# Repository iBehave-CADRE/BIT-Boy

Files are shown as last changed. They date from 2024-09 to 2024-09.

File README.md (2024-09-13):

# BITboy

A handheld oscilloscope and behavioral setup debugger for neuroscientists. Your every-day companion for trouble shooting and setting up experimental instruments.

Read and write both analog and digital signals with ease. Check continuity in electronic circuits with the continuity checker. It can be used as a handheld oscilloscope or connected to your pc on a desk for higher resolution.

General disclaimer: Our BITboy is designed to work in a range of 0-5V and will take damage if connected to higher loads. Therefore, please be careful. We are planning a future version with overvoltage protection.

<p align="center">
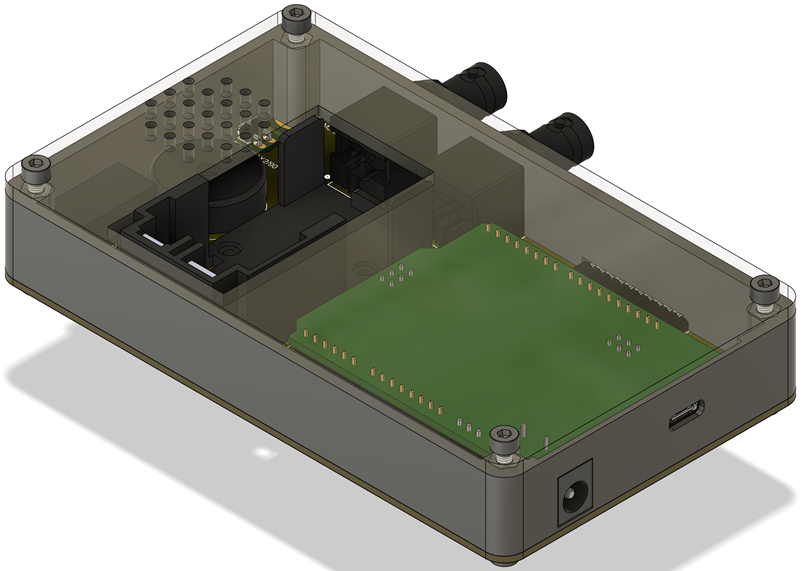
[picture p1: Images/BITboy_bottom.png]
  
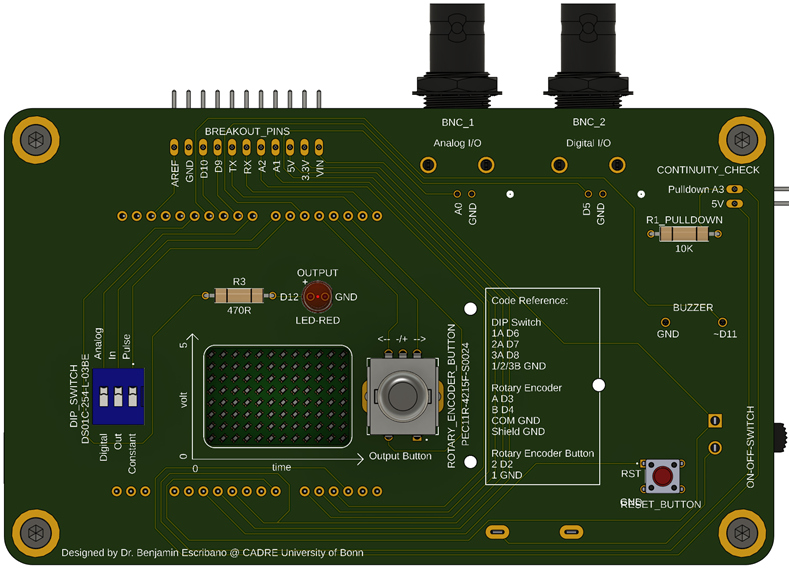
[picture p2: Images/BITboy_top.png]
  
</p>

All provided files are in metric units (mm). The case can be 3D printed, while the cover can be lasercut or printed. The design aims at maximum reproduxibility with low total cost.

### Commercial Parts List

| Item | Quantity | Notes | Product Example Link |
| :---: | :---: | :---: | :---: |
| PCB | 1 piece | [custom design](PCB) | [eurocircuits.com](https://www.eurocircuits.com/) |
| Arduino UNO R4 Wifi | 1 piece | with LED matrix | [arduino.cc](https://store.arduino.cc/en-de/collections/boards-modules/products/uno-r4-wifi) |
| Pin Header 90 degrees | bar of 1x11 & 1x2 | attached | [conrad.de](https://www.conrad.de/de/p/econ-connect-stiftleiste-standard-anzahl-reihen-1-polzahl-je-reihe-40-sl25ws40gc-1-st-1883758.html) |
| Pin Header | bar of 1x6, 2x 1x8 & 1x10 | attached | [conrad.de](https://www.conrad.de/de/p/econ-connect-stiftleiste-standard-anzahl-reihen-1-polzahl-je-reihe-6-sl6g1-1-st-1884013.html) |
| Battery Holder | 1 piece | BC9VPC | [digikey.de](https://www.digikey.de/de/products/detail/mpd-memory-protection-devices/BC9VPC/257747) |
| Screw M2x8 mm | 3 pieces | for battery holder | [mercateo.com](https://www.mercateo.com/p/2805-M2X8(2f)D912(2d)A2/Schraube_M2x8_0_4_Kopf_Zylinder_Sechskant_HEX_1_5mm_DIN_912.html?ViewName=live~secureMode&chooseGeo=true&viewOptions=uiLanguage.en) |
| Nut M2 | 3 pieces | for battery holder | [digikey.de](https://www.mercateo.com/p/2805-B2(2f)BN628/Mutter_Sechskant_M2_0_4_A2_Edelstahl_4mm_BN_628_DIN_934.html?ViewName=live~secureMode!uiLanguage.en) |
| Washer M2 | 3 pieces | for battery holder | [digikey.de](https://www.mercateo.com/p/4502-16H910/Unterlegscheibe_M2_H_0_35_mm_Aussen_4_mm_Stahl_verzinkt_DIN_433_ISO_7092_.html?ViewName=live~secureMode!uiLanguage.en) |
| 9V Block Battery | 1 piece |  | [conrad.de](https://www.conrad.de/de/p/varta-longlife-power-9v-bli-2-9-v-block-batterie-alkali-mangan-580-mah-9-v-2-st-1012376.html) |
| On-Off Switch | 1 piece | L101011ML04Q | [digikey.de](https://www.digikey.de/de/products/detail/c-k/L101011ML04Q/3753550?s=N4IgTCBcDaIDIEYAMyEILJyQFgIogF0BfIA) |
| Rotary Encoder | 1 piece | PEC11R-4215F-S0024-ND | [digikey.de](https://www.digikey.de/de/products/detail/bourns-inc/PEC11R-4215F-S0024/4499665?s=N4IgTCBcDaIAoFEDCBGFAlAtAFjCgrAGKYDKADGWNiALoC%2BQA) |
| DIP Switch | 1 piece | DS01C-254-L-03BE | [digikey.de](https://www.digikey.de/de/products/detail/cui-devices/DS01C-254-L-03BE/11310858?s=N4IgTCBcDaICIGUAMBGAwgWjAVgCwYBkMkBmAIQFEQBdAXyA) |
| Piezo Buzzer | 1 piece | 490-4692-ND | [digikey.de](https://www.digikey.de/de/products/detail/murata-electronics/PKM22EPPH4001-B0/1219323?s=N4IgTCBcDaIAoGkCyYwFE5wBIBYAMeAjALQBCeIAugL5A) |
| Red LED | 1 piece | set of 100 | [conrad.de](https://www.conrad.de/de/p/led-5mm-rot-led5mm-rot-tht-leuchtdiode-set-100-stueck-847144284.html) |
| Tactile Switch | 1 piece | 450-1650-ND | [digikey.de](https://www.digikey.de/de/products/detail/te-connectivity-alcoswitch-switches/1825910-6/1632536) |
| BNC Connector | 1 piece | ARF1690-ND | [digikey.de](https://www.digikey.de/de/products/detail/amphenol-rf/031-5431-10RFX/2041816?s=N4IgTCBcDaIAwGYCMBaArAFmSpcBKAYgBogC6AvkA) |
| 470R Resistor | 1 piece | for LED | [conrad.de](https://www.conrad.de/de/p/yageo-cfr25j470rh-cfr-25jt-52-470r-kohleschicht-widerstand-470-axial-bedrahtet-0207-0-25-w-5-1-st-1417694.html) |
| 10K Resistor | 1 piece | puldown for continuity check | [digikey.de](https://www.conrad.de/de/p/yageo-cfr25j10kh-cfr-25jt-52-10k-kohleschicht-widerstand-10-k-axial-bedrahtet-0207-0-25-w-5-1-st-1417697.html) |
| Jumper Male-Female | 2 wires | for continuity check | [conrad.de](https://www.conrad.de/de/p/renkforce-jkmf403-jumper-kabel-arduino-banana-pi-raspberry-pi-40x-drahtbruecken-stecker-40x-drahtbruecken-buchse-30-2299844.html) |

### Case Parts

| Item | Quantity | Notes | Product Example Link |
| :---: | :---: | :---: | :---: |
| Case | 1 piece | [custom design](Case/BITboy_Case.stl) | 3D printed |
| Acrylic Cover (3 mm) | 1 piece | [custom design](Case/BITboy_Acrylic_Cover.stl) | lasercut, can be printed |
| Screw M3x10 mm | 8 pieces | self-tapping | [mercateo.com](https://www.mercateo.com/p/1498C-8000152817/Flachkopfschraube_DIN_85_ISO_1580_Schlitz_M3x10_4_8_galv_verz_200St_.html?ViewName=live~secureMode) |
| Washer M3 | 8 pieces |  | [mercateo.com](https://www.mercateo.com/p/4502-16H900/Unterlegscheibe_M3_H_0_5_mm_Aussen_7_mm_Stahl_verzinkt_DIN_125_ISO_7090_.html?ViewName=live~secureMode) |

All files are available as .STEP (for 3D CAD), .DXF Files (scaling: 1pt equals 1mm for laser cutting), .STL (3D Object for Printing). Electronics are provided as fusion arcive files (.f3z) and gerber files for PCB production with eurocircuits.

Wiring Diagram
--------------------
<p align="center">
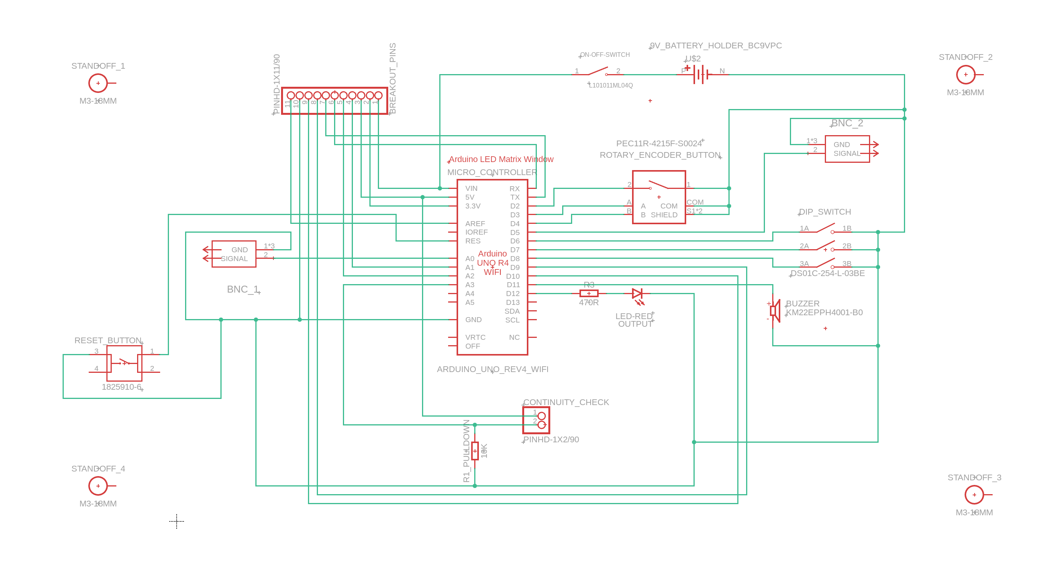
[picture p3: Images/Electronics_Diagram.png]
  
</p>

PCB Layout
--------------------
<p align="center">
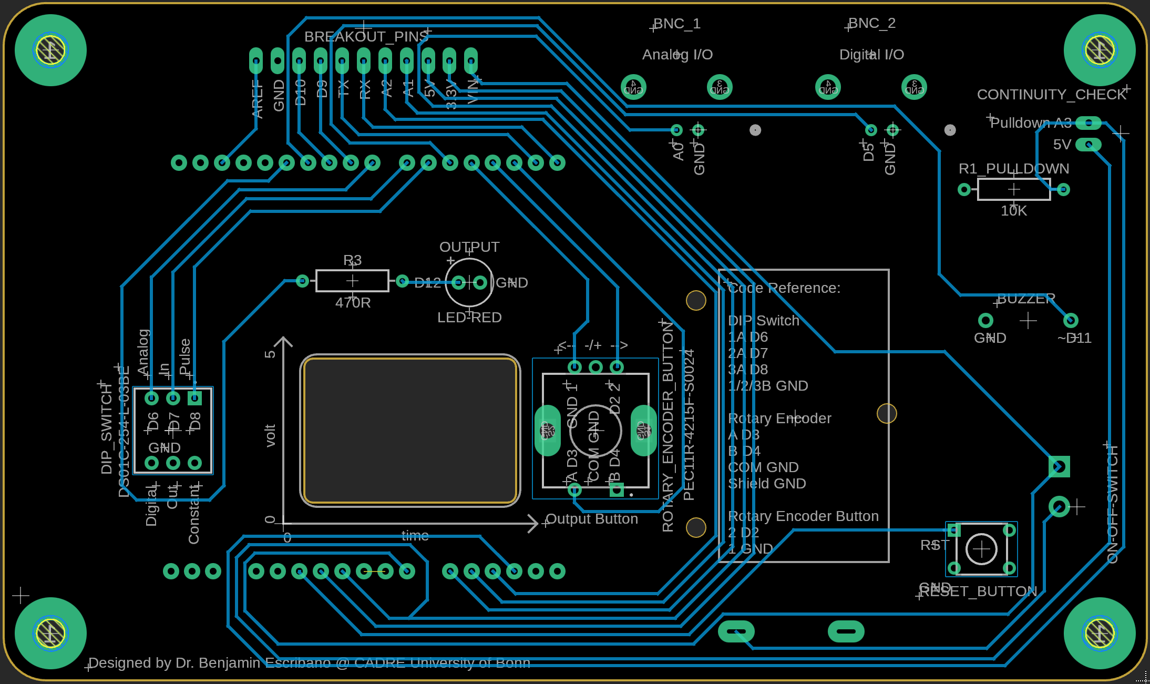
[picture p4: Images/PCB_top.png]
  
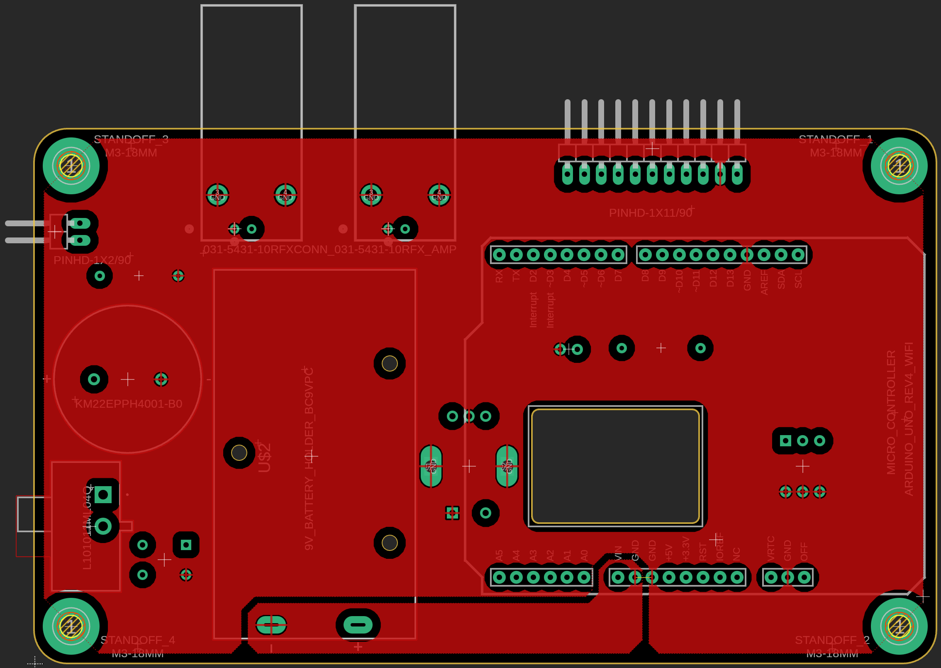
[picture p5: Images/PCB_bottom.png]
  
</p>

Pin Layout
--------------------

### Red LED

| Arduino Pin | Connected to | Note |
| :---: | :---: | :---: |
| D12 | red LED + (long) | via 470R resistor |
| GND | red LED - |  |

### Piezo Buzzer

| Arduino Pin | Connected to | Note |
| :---: | :---: | :---: |
| D11 | piezzo buzzer + | PWM (pulse width modulation) |
| GND | piezzo buzzer - |  |

### BNC 1 Analog I/O

| Arduino Pin | Connected to | Note |
| :---: | :---: | :---: |
| A0 | BNC connector signal pin | for DAC |
| GND | BNC connector shield/GND |  |

### BNC 2 Digital I/O

| Arduino Pin | Connected to | Note |
| :---: | :---: | :---: |
| D5 | BNC connector signal pin |  |
| GND | BNC connector shield/GND |  |

### DIP Switch (Dual in-line package)

| Arduino Pin | Connected to | Note |
| :---: | :---: | :---: |
| D6 | 1 A |  |
| D7 | 2 A |  |
| D8 | 3 A |  |
| GND | 1/2/3 B |  |

### Rotary Encoder with Button

| Arduino Pin | Connected to | Note |
| :---: | :---: | :---: |
| D2 | button 2 | interrupt pin |
| GND | button 1 |  |
| D3 | encoder A | interrupt pin |
| D4 | encoder B |  |
| GND | encoder shield & COM |  |

### Continuity Check

| Arduino Pin | Connected to | Note |
| :---: | :---: | :---: |
| A3 | 1x2 pin header | with 10K pulldown resistor to GND |
| 5V | 1x2 pin header |  |

### Reset Button

| Arduino Pin | Connected to | Note |
| :---: | :---: | :---: |
| RST | tactile switch A |  |
| GND | tactile switch B |  |

[Here you find an example for using the RST pin with a tactile switch](https://www.circuitschools.com/external-reset-button-for-arduino-or-reset-arduino-with-code/)

### ON-OFF Switch and Battery

| Arduino Pin | Connected to | Note |
| :---: | :---: | :---: |
| VIN | switch + |  |
| battery holder + | switch - |  |
| GND | battery holder - |  |

[Here you find more about powering options for Arduinos](https://docs.arduino.cc/learn/electronics/power-pins/)

[Here you find an example and pictures for powering with a battery](https://www.instructables.com/Powering-Arduino-with-a-Battery/)

### Breakout Pins

| Arduino Pin | Connected to | Note |
| :---: | :---: | :---: |
| AREF | 1x11 pin header | for custom code |
| GND | 1x11 pin header | for custom code |
| D10 | 1x11 pin header | for custom code |
| D9 | 1x11 pin header | for custom code |
| TX | 1x11 pin header | for custom code |
| RX | 1x11 pin header | for custom code |
| A2 | 1x11 pin header | for custom code |
| A1 | 1x11 pin header | for custom code |
| 5V | 1x11 pin header | for custom code |
| 3.3V | 1x11 pin header | for custom code |
| VIN | 1x11 pin header | for custom code |

BITboy Control Logic
--------------------

Each reset/reboot of the device will start a readout procedure of the DIP switch to determine one of six operational settings modes.

The following table provides an overview about individual modules and their task during each mode:

| Module | Analog In Pulse/Constant | Analog Out Pulse | Analog Out Constant |Digital In Pulse/Constant | Digital Out Pulse | Digital Out Constant |
| :---: | :---: | :---: | :---: | :---: | :---: | :---: |
| **BNC_1 Analog I/O** | Analog Read | Analog Write | Analog Write | Idle | Idle | Idle |
| **BNC_2 Digital I/O** | Idle | Idle | Idle | Digital Read | Digital Write | Digital Write |
| **Rotary Encoder** | Temporal Resolution | Set Voltage | Set Voltage | Temporal Resolution | Idle | Idle |
| **Rotary Button** | Idle | Hold | Toggle | Idle | Hold | Toggle |
| **Output LED-Red** | Idle | Write Indicator | Write Indicatr | Idle | Write Indicator | Write Indicator |
| **Buzzer** | Coupled Continuity |  |  |  |  |  |
| **LED Matrix** | Analog Voltage | Analog Voltage | Analog Voltage | Digital Voltage | Digital Voltage | Digital Voltage |
| **Continuity Check** | Active | Active | Active | Active | Active | Active |
| **Breakout Pins** | Idle | Idle | Idle | Idle | Idle | Idle |

Lasercutting
--------------------

We used a Trotec Speedy Flex lasercutter with a 100W CO2 laser with the following settings for 3 mm acrylic glass:

| Parameter | Cutting Quality |
| :---: | :---: |
| Power | 40 Watts |
| Speed | 0,2 % |
| Laser Source | CO2 |
| Frequency | 20000 |
| Passes | 1 |
| Power Correction | 10 |
| z-Offset | 0 |

3D Printing
--------------------
We suggest printing with PLA, tough PLA or ABS for best results. Any standard print settings will provide aceptable results. Avoid fancy materials to reduce cost and effort.

For the case, we used a Babulab A1 mini filament printer with generic PLA.

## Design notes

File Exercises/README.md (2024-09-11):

# Exercises

Serial Printing is you most powerful debugging tool when coding your device.

You will have to install the Arudino IDE and copy paste the code from here to the sketch. Then compile and upload.

Sometimes the Arduino requires an additional driver installation

Easy and medium are thought in a way that you can make each individual function work individually. Each excersise can be an individual code. You can try to make modules while coding thisn. And then in hard the task is to bring the individual functions to gether and make them work all at once.

Be careful, do not use more than 5V on the BNCs, since we do not have an überspannungs schutz.

## Easy

### 1. Make the LED Blink

```C++
void setup() {
  // put your setup code here, to run once:
  // use semicolons after each line!

}

void loop() {
  // put your main code here, to run repeatedly:
  // use semicolons after each line!

}
```
Useful functions for this exercise:

```C++
digitalWrite(pin, value)
```

pin: Die Arduino-Pinnummer.
value: HIGH oder LOW.

[Documentation](https://www.arduino.cc/reference/de/language/functions/digital-io/digitalwrite/)

```C++
pinMode(pin, mode)
```

pin: the Arduino pin number to set the mode of.
mode: INPUT, OUTPUT, or INPUT_PULLUP.

[Documentation](https://www.arduino.cc/reference/en/language/functions/digital-io/pinmode/)

delay(ms)
ms: the number of milliseconds to pause. Allowed data types: unsigned long.

int ledPin = 13;              // LED connected to digital pin 13

void setup() {
  pinMode(ledPin, OUTPUT);    // sets the digital pin as output
}

void loop() {
  digitalWrite(ledPin, HIGH); // sets the LED on
  delay(1000);                // waits for a second
  digitalWrite(ledPin, LOW);  // sets the LED off
  delay(1000);                // waits for a second
}

### 2. Make the Buzzer Beep or Play a Melody

### 3. Plot an Image on the LED Matrix

### 4. Write an Analog or Digital Signal

## Medium

### 1. Read an Analog or Digital Signal and Plot it via Serial Communication

### 2. Implement the Continuity Check

### 3. Implement the DIP Switch

### 4. Implement the Rotary Encoder with Button

### 5. Implement the Rotary Encoder with Button

## Hard

### 1. Read an Analog or Digital and Plot it on the LED Matrix Display

### 2. Combine All Modules and Make them Work Together

Useful Resources
--------------------
variables etc.
pullup and pulldown resistors
Built in functions and Operators
Arduino Functions
DigitalRead/Write
Rotary encoder example
Buzzer example
LED example
DIP switch example
Reset button example
Power via Battery example
Continuity check example
BNC example

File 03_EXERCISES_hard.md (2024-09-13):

## Exercises Hard

### 1. Read an Analog Signals and Plot it on the LED Matrix Display

```C++
void setup() {

}

void loop() {

}

//Useful functions for this exercise:

pinMode(pin, mode)
//pin: the Arduino pin number to set the mode of.
//mode: INPUT, OUTPUT, or INPUT_PULLUP.

analogReadResolution(bits);
//Can be set to 10 or 13 bits for read resolution (0-1023 for 10 bits or 0-4095 for 12 bits).

analogRead(pin)
//pin: the name of the analog input pin to read from.
//Returns the analog reading on the pin.
//Data type: int.

map(value, fromLow, fromHigh, toLow, toHigh)
//value: the number to map.
//fromLow: the lower bound of the value’s current range.
//fromHigh: the upper bound of the value’s current range.
//toLow: the lower bound of the value’s target range.
//toHigh: the upper bound of the value’s target range.

constrain(x, a, b)
//x: the number to constrain Allowed data types: all data types.
//a: the lower end of the range. Allowed data types: all data types.
//b: the upper end of the range. Allowed data types: all data types.
//Returns x: if x is between a and b. /a: if x is less than a. /b: if x is greater than b.

Serial.begin(speed)
//Serial: serial port object.
//speed: in bits per second (baud). Allowed data types: long.

Serial.print(val)
//Serial: serial port object.
//val: the value to print. Allowed data types: any data type.

Serial.println(val) //Serial println adds characters for printing in a new line
//Serial: serial port object.
//val: the value to print. Allowed data types: any data type.

//You will have to include the LED matrix library
#include "Arduino_LED_Matrix.h"

Serial.begin(speed)
//speed: in bits per second (baud). Allowed data types: long.

//start the LED Matrix by adding this line in void setup:
matrix.begin();

//This is how you can make a two-dimensional array of bytes to encode an image:
uint8_t BootScreen[8][12] = {};

//This is how you can render and display your two-dimensional array as an image:
matrix.renderBitmap(BootScreen, 8, 12);

delay(ms)
//ms: the number of milliseconds to pause. Allowed data types: unsigned long.
```

[Here you will a possible solution](Exercise_Solutions/03_Hard/01_Plot_Analog.md)

### 2. Combine All Modules and Make them Work Together

```C++
void setup() {

}

void loop() {

}
//Useful functions for this exercise:

//If you are here, you know hot to navigate Arduino documentation and coding language references ;-)
```

[Here you will find the finished firmware](Firmware/BITboy)

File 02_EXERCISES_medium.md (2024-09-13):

DIP switch example

## Exercises Medium

### 1. Read an Analog or Digital Signal and Plot it via Serial Communication

```C
void setup() {
  // put your setup code here, to run once:
  // use semicolons after each line!

}

void loop() {
  // put your main code here, to run repeatedly:
  // use semicolons after each line!

}

//Useful functions for this exercise:

pinMode(pin, mode)
//pin: the Arduino pin number to set the mode of.
//mode: INPUT, OUTPUT, or INPUT_PULLUP.

analogReadResolution(bits);
//Can be set to 10 or 13 bits for read resolution (0-1023 for 10 bits or 0-4095 for 12 bits).

analogRead(pin)
//pin: the name of the analog input pin to read from.
//Returns the analog reading on the pin.
//Data type: int.

digitalRead(pin)
//pin: the Arduino pin number you want to read
// Returns HIGH or LOW

map(value, fromLow, fromHigh, toLow, toHigh)
//value: the number to map.
//fromLow: the lower bound of the value’s current range.
//fromHigh: the upper bound of the value’s current range.
//toLow: the lower bound of the value’s target range.
//toHigh: the upper bound of the value’s target range.

constrain(x, a, b)
//x: the number to constrain Allowed data types: all data types.
//a: the lower end of the range. Allowed data types: all data types.
//b: the upper end of the range. Allowed data types: all data types.
//Returns x: if x is between a and b. /a: if x is less than a. /b: if x is greater than b.

Serial.begin(speed)
//Serial: serial port object.
//speed: in bits per second (baud). Allowed data types: long.

Serial.print(val)
//Serial: serial port object.
//val: the value to print. Allowed data types: any data type.

Serial.println(val) //Serial println adds characters for printing in a new line
//Serial: serial port object.
//val: the value to print. Allowed data types: any data type.

delay(ms)
//ms: the number of milliseconds to pause. Allowed data types: unsigned long.
```

[Here you will find a possible solution](Exercise_Solutions/02_Medium/01_Analog_Digital_Read_Serial.md)

### 2. Implement the Continuity Check

The continuity check allows you to test whether two parts are connected between two pins. If there is continuity, 5V can flow to pin A3 and pull it to a HIGH state. The pulldown resistor ensures a stable reading of the LOW state. Write a code that makes the buzzer beep when there is continuity between the 5V pin and the A3 pin. You can use A3 as a digital pin for simplicity.

```C++

void setup() {

}

void loop() {

}

//Useful functions for this exercise:

pinMode(pin, mode)
//pin: the Arduino pin number to set the mode of.
//mode: INPUT, OUTPUT, or INPUT_PULLUP.

digitalRead(pin)
//pin: the Arduino pin number you want to read
// Returns HIGH or LOW

tone(pin, frequency)
tone(pin, frequency, duration)
//pin: the Arduino pin on which to generate the tone.
//frequency: the frequency of the tone in hertz. Allowed data types: unsigned int.
//duration: the duration of the tone in milliseconds (optional). Allowed data types: unsigned long.

noTone(pin)
//pin: the Arduino pin on which to stop generating the tone

//You can use an if/else if loop for this task
if (condition1) {
  // do Thing A
}
else if (condition2) {
  // do Thing B
}
else {
  // do Thing C
}
//condition: a boolean expression (i.e., can be true or false).

delay(ms)
//ms: the number of milliseconds to pause. Allowed data types: unsigned long.
```

[Here you will find a possible solution](Exercise_Solutions/02_Medium/02_Continuity_Check.md)

[Here you find information about using pullup and pulldown resistors](https://arduinogetstarted.com/faq/arduino-pull-up-pull-down-resistor)

### 3. Implement the DIP Switch

The DIP switch is used to set the BITBoy's function when powered on. Its state is read out to assign a preset when booting the device. You can implement the code in the setup section to only read it once and serial print the mode. Resetting will allow a new readout.

```C++

void setup() {

}

void loop() {

}

//Useful functions for this exercise:

pinMode(pin, mode)
//pin: the Arduino pin number to set the mode of.
//mode: INPUT, OUTPUT, or INPUT_PULLUP.

digitalRead(pin)
//pin: the Arduino pin number you want to read
// Returns HIGH or LOW

for (initialization; condition; increment) {
  // statement(s);
}
//initialization: happens first and exactly once.
//condition: each time through the loop, condition is tested; if it’s true, the statement block, and the increment is executed, then the condition is tested again. When the condition becomes false, the loop ends.
//increment: executed each time through the loop when condition is true.

strcat(string1, string2);
//Concatenates string1 with string1. Input tye char.
//Returns concatenated string char.

return value;
//value: Allowed data types: any variable or constant type.

//You can use an if/else if loop for this task
if (condition1) {
  // do Thing A
}
else if (condition2) {
  // do Thing B
}
else {
  // do Thing C
}
//condition: a boolean expression (i.e., can be true or false).

Serial.begin(speed)
//Serial: serial port object.
//speed: in bits per second (baud). Allowed data types: long.

Serial.print(val)
//Serial: serial port object.
//val: the value to print. Allowed data types: any data type.

Serial.println(val) //Serial println adds characters for printing in a new line
//Serial: serial port object.
//val: the value to print. Allowed data types: any data type.
```

[Here you will find a possible solution](Exercise_Solutions/02_Medium/03_DIP_Switch.md)

[Here you find more information about DIP switches](https://arduinogetstarted.com/tutorials/arduino-dip-switch)

### 4. Implement the Rotary Encoder with Button

```C++
void setup() {
  
}

void loop() {

}

pinMode(pin, mode)
//pin: the Arduino pin number to set the mode of.
//mode: INPUT, OUTPUT, or INPUT_PULLUP.

digitalRead(pin)
//pin: the Arduino pin number you want to read
// Returns HIGH or LOW

digitalWrite(pin, value)
//pin: Arduino-Pinnummer.
//value: HIGH or LOW.

return value;
//value: Allowed data types: any variable or constant type.

//You can use an if/else if loop for this task
if (condition1) {
  // do Thing A
}
else if (condition2) {
  // do Thing B
}
else {
  // do Thing C
}

millis()
//Returns the number of milliseconds passed since the Arduino board began running the current program. This number will overflow (go back to zero), after approximately 50 days.

Serial.begin(speed)
//Serial: serial port object.
//speed: in bits per second (baud). Allowed data types: long.

Serial.print(val)
//Serial: serial port object.
//val: the value to print. Allowed data types: any data type.

Serial.println(val) //Serial println adds characters for printing in a new line
//Serial: serial port object.
//val: the value to print. Allowed data types: any data type.

attachInterrupt(digitalPinToInterrupt(pin), ISR, mode)
//interrupt: the number of the interrupt. Allowed data types: int.
//pin: the Arduino pin number.
//ISR: the ISR to call when the interrupt occurs; this function must take no parameters and return nothing. This function is sometimes referred to as an interrupt service routine.
//mode: defines when the interrupt should be triggered. Four constants are predefined as valid values: LOW, CHANGE, RISING, FALLING.
```

[Here you will find a possible solution](Exercise_Solutions/02_Medium/04_Rotary_Button.md)

[Here you find information about attaching an interrupt](https://www.arduino.cc/reference/en/language/functions/external-interrupts/attachinterrupt/)

[Here you find information rotary encoders](https://arduinogetstarted.com/tutorials/arduino-rotary-encoder)

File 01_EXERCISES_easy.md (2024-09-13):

## Exercises Easy

### 1. Make the LED Blink

```C
void setup() {
  // put your setup code here, to run once:
  // use semicolons after each line!

}

void loop() {
  // put your main code here, to run repeatedly:
  // use semicolons after each line!

}

//Useful functions for this exercise:

pinMode(pin, mode)
//pin: the Arduino pin number to set the mode of.
//mode: INPUT, OUTPUT, or INPUT_PULLUP.

digitalWrite(pin, value)
//pin: Arduino-Pinnummer.
//value: HIGH or LOW.

delay(ms)
//ms: the number of milliseconds to pause. Allowed data types: unsigned long.
```

[Here you will find a possible solution](Exercise_Solutions/01_Easy/01_Make_LED_Blink.md)

### 2. Make the Buzzer Beep (or Play a Melody if you feel like it)

```C
void setup() {
  // put your setup code here, to run once:

}

void loop() {
  // put your main code here, to run repeatedly:

}

//Useful functions for this exercise:

tone(pin, frequency)
tone(pin, frequency, duration)
//pin: the Arduino pin on which to generate the tone.
//frequency: the frequency of the tone in hertz. Allowed data types: unsigned int.
//duration: the duration of the tone in milliseconds (optional). Allowed data types: unsigned long.

noTone(pin)
//pin: the Arduino pin on which to stop generating the tone

delay(ms)
//ms: the number of milliseconds to pause. Allowed data types: unsigned long.
```

[Here you will find a possible solution](Exercise_Solutions/01_Easy/02_Make_Buzzer_Beep.md)

[Check out this link if you want to know how to play a melody](https://docs.arduino.cc/built-in-examples/digital/toneMelody/)

### 3. Write Analog or Digital Signals and Test it on the Oscilloscope

```C
void setup() {
  // put your setup code here, to run once:

}

void loop() {
  // put your main code here, to run repeatedly:

}

//Useful functions for this exercise:

pinMode(pin, mode)
//pin: the Arduino pin number to set the mode of.
//mode: INPUT, OUTPUT, or INPUT_PULLUP.

digitalWrite(pin, value)
//pin: Arduino-Pinnummer.
//value: HIGH or LOW.

analogWrite(pin, value)
//pin: the Arduino pin to write to. Allowed data types: int.
//value: the duty cycle: between 0 (always off) and 255 (always on). Allowed data types: int.

```

[Here you will find a possible solution](Exercise_Solutions/01_Easy/03_Write_Analog_Digital_Signals.md)

### 4. Plot an Image on the LED Matrix (or display an animation if you feel like it)

```C
void setup() {
  // put your setup code here, to run once:

}

void loop() {
  // put your main code here, to run repeatedly:

}

//Useful functions for this exercise:

//You will have to include the LED matrix library
#include "Arduino_LED_Matrix.h"

Serial.begin(speed)
//speed: in bits per second (baud). Allowed data types: long.

//start the LED Matrix by adding this line in void setup:
matrix.begin();

//This is how you can make a two-dimensional array of bytes to encode an image:
uint8_t BootScreen[8][12] = {
  { 0, 0, 0, 0, 0, 0, 1, 0, 0, 0, 0, 0 },
  { 0, 0, 0, 0, 0, 1, 1, 0, 0, 0, 0, 0 },
  { 0, 0, 0, 0, 1, 0, 1, 0, 0, 0, 0, 0 },
  { 0, 0, 0, 0, 1, 0, 1, 0, 0, 0, 0, 0 },
  { 0, 0, 0, 1, 0, 0, 1, 0, 0, 0, 0, 0 },
  { 1, 1, 1, 1, 0, 0, 1, 0, 1, 1, 1, 1 },
  { 0, 0, 0, 0, 0, 0, 1, 1, 0, 0, 0, 0 },
  { 0, 0, 0, 0, 0, 0, 1, 0, 0, 0, 0, 0 }
};

//This is how you can render and display your two-dimensional array as an image:
matrix.renderBitmap(BootScreen, 8, 12);

```

[More about arrays here](https://www.arduino.cc/reference/en/language/variables/data-types/array/)

[Here you will find a simple solution](Exercise_Solutions/01_Easy/04_Make_LED_Matrix_Image.md)

[Check out this link if you want to know how to play a more complex Animation ](https://docs.arduino.cc/tutorials/uno-r4-wifi/led-matrix/)

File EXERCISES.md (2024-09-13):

# Exercises

Serial Printing is you most powerful debugging tool when coding your device.

You will have to install the Arudino IDE and copy paste the code from here to the sketch. Then compile and upload.

[Download Arduino IDE](https://www.arduino.cc/en/software)

Sometimes the Arduino requires an additional driver installation. 

Easy and medium are thought in a way that you can make each individual function work individually. Each excersise can be an individual code. You can try to make modules while coding thisn. And then in hard the task is to bring the individual functions to gether and make them work all at once.

Be careful, do not use more than 5V on the BNCs, since we do not have an überspannungs schutz.

Useful Resources
--------------------
Here you can find a complete language reference, built in functions, variable types and structural operators:

[Arduino Language Reference](https://www.arduino.cc/reference/en/)

pullup and pulldown resistors
Rotary encoder example
Buzzer example
LED example
DIP switch example
Reset button example
Power via Battery example
Continuity check example
BNC example

## Easy

### 1. Make the LED Blink

```C
void setup() {
  // put your setup code here, to run once:
  // use semicolons after each line!

}

void loop() {
  // put your main code here, to run repeatedly:
  // use semicolons after each line!

}

//Useful functions for this exercise:

digitalWrite(pin, value)
//pin: Arduino-Pinnummer.
//value: HIGH or LOW.

pinMode(pin, mode)
//pin: the Arduino pin number to set the mode of.
//mode: INPUT, OUTPUT, or INPUT_PULLUP.

delay(ms)
//ms: the number of milliseconds to pause. Allowed data types: unsigned long.
```

[Here you will find a possible solution](Exercise_Solutions/01_Easy/01_Make_LED_Blink.md)

### 2. Make the Buzzer Beep (or Play a Melody if you feel like it)

```C
void setup() {
  // put your setup code here, to run once:

}

void loop() {
  // put your main code here, to run repeatedly:

}

//Useful functions for this exercise:

tone(pin, frequency)
tone(pin, frequency, duration)
//pin: the Arduino pin on which to generate the tone.
//frequency: the frequency of the tone in hertz. Allowed data types: unsigned int.
//duration: the duration of the tone in milliseconds (optional). Allowed data types: unsigned long.

noTone(pin)
//pin: the Arduino pin on which to stop generating the tone

delay(ms)
//ms: the number of milliseconds to pause. Allowed data types: unsigned long.
```

[Here you will find a possible solution](Exercise_Solutions/01_Easy/02_Make_Buzzer_Beep.md)

[Check out this link if you want to know how to play a melody](https://docs.arduino.cc/built-in-examples/digital/toneMelody/)

### 3. Plot an Image on the LED Matrix (or display an animation if you feel like it)

```C
void setup() {
  // put your setup code here, to run once:

}

void loop() {
  // put your main code here, to run repeatedly:

}

//Useful functions for this exercise:

//You will have to include the LED matrix library
#include "Arduino_LED_Matrix.h"

Serial.begin(speed)
//speed: in bits per second (baud). Allowed data types: long.

//start the LED Matrix by adding this line in void setup:
matrix.begin();

//This is how you can make a two-dimensional array of bytes to encode an image:
uint8_t BootScreen[8][12] = {
  { 0, 0, 0, 0, 0, 0, 1, 0, 0, 0, 0, 0 },
  { 0, 0, 0, 0, 0, 1, 1, 0, 0, 0, 0, 0 },
  { 0, 0, 0, 0, 1, 0, 1, 0, 0, 0, 0, 0 },
  { 0, 0, 0, 0, 1, 0, 1, 0, 0, 0, 0, 0 },
  { 0, 0, 0, 1, 0, 0, 1, 0, 0, 0, 0, 0 },
  { 1, 1, 1, 1, 0, 0, 1, 0, 1, 1, 1, 1 },
  { 0, 0, 0, 0, 0, 0, 1, 1, 0, 0, 0, 0 },
  { 0, 0, 0, 0, 0, 0, 1, 0, 0, 0, 0, 0 }
};

//This is how you can render and display your two-dimensional array as an image:
matrix.renderBitmap(BootScreen, 8, 12);

```

[More about arrays here](https://www.arduino.cc/reference/en/language/variables/data-types/array/)

[Here you will find a simple solution](Exercise_Solutions/01_Easy/03_Make_LED_Matrix_Image.md)

[Check out this link if you want to know how to play a more complex Animation ](https://docs.arduino.cc/tutorials/uno-r4-wifi/led-matrix/)

### 4. Write an Analog or Digital Signal

## Medium

### 1. Read an Analog or Digital Signal and Plot it via Serial Communication

### 2. Implement the Continuity Check

### 3. Implement the DIP Switch

### 4. Implement the Rotary Encoder with Button

### 5. Implement the Rotary Encoder with Button

## Hard

### 1. Read an Analog or Digital and Plot it on the LED Matrix Display

### 2. Combine All Modules and Make them Work Together

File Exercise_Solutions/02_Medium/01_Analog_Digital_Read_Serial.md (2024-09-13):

```C++
//BNC Port Definitions
#define version "1"

#define AnalogDataPin A0
#define DigitalDataPin D5   

//Initialising variables for later use in the script
int MeasuredDigitalInput;
int MeasuredAnalogInput;

void setup() {
  //Setting the resolution to 12 will read in a range of 0-4095, while setting to 10 will read 0-1023
  analogReadResolution(12);
  pinMode(AnalogDataPin, INPUT);
  //Test and see what happens if you use INPUT_PULLUP here...
  pinMode(DigitalDataPin, INPUT);
  //Start serial communication
  Serial.begin(115200);
  Serial.print("BITboy Interface Version ");
  Serial.println(version);
}

void loop() {
  //Reaging analog input and mapping it to 5V for serial print with accurate units.
  MeasuredAnalogInput = map(analogRead(AnalogDataPin), 0, 4095, 0, 5);
  MeasuredAnalogInput = constrain(MeasuredAnalogInput, 0, 5);

  //Reaging digital input and mapping it to 5V for serial print with accurate units.
  MeasuredDigitalInput = map(digitalRead(DigitalDataPin), 0, 1, 0, 5);
  MeasuredDigitalInput = constrain(MeasuredDigitalInput, 0, 5);

  delay(200);

  //Serial printing of analog signal. The first print will allow to name the variable in the serial plotter.
  Serial.print("Analog_In[V]:");
  Serial.println(MeasuredAnalogInput);
  //Serial printing of digital signal. The first print will allow to distinguish the secont variable from the first print in the plotter.
  Serial.print("Digital_In[V]:");
  Serial.println(MeasuredDigitalInput);
}
```

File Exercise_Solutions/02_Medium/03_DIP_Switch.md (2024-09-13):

```C++
#define version "1"

//DIP Switch
#define DIPSwitch1 6
#define DIPSwitch2 7
#define DIPSwitch3 8
#define DIPSwitchPositions 3

#define ON LOW
#define OFF HIGH

#define Digital " Digital"
#define Analog " Analog"
#define Out " Output"
#define In " Input"
#define Constant " Constant"
#define Pulse " Pulse"

int DIPSwitchSetting = 0;
int DIPPinState = 0;
char SettingsText[25];
int Mode = 0;

const int DIPSwitchPins[3] = {DIPSwitch1, DIPSwitch2, DIPSwitch3};

void setup() {
  Serial.begin(115200);
  Serial.print("BITboy Interface Version ");
  Serial.println(version);
    for (int i = 0; i < DIPSwitchPositions; i++) {
        pinMode(DIPSwitchPins[i], INPUT_PULLUP);
    }
    Mode = ReadDIPSwitchSettings();
    Serial.println(Mode);
}

void loop() {
}

int ReadDIPSwitchSettings() {
  for (int i = 0; i < DIPSwitchPositions; i++) {
    DIPPinState = digitalRead(DIPSwitchPins[i]);

    if (DIPPinState == ON)
      DIPSwitchSetting |= 1 << (DIPSwitchPositions - i - 1);
  }

  if (DIPSwitchSetting == 0) {
    strcat(SettingsText, Digital);
    strcat(SettingsText, Out);
    strcat(SettingsText, Constant);
  } else if (DIPSwitchSetting == 1) {
    strcat(SettingsText, Analog);
    strcat(SettingsText, Out);
    strcat(SettingsText, Constant);
  } else if (DIPSwitchSetting == 2 || DIPSwitchSetting == 6) {
    strcat(SettingsText, Digital);
    strcat(SettingsText, In);
  } else if (DIPSwitchSetting == 3 || DIPSwitchSetting == 7) {
    strcat(SettingsText, Analog);
    strcat(SettingsText, In);
  } else if (DIPSwitchSetting == 4) {
    strcat(SettingsText, Digital);
    strcat(SettingsText, Out);
    strcat(SettingsText, Pulse);
  } else if (DIPSwitchSetting == 5) {
    strcat(SettingsText, Analog);
    strcat(SettingsText, Out);
    strcat(SettingsText, Pulse);
  }

  Serial.print("BITboy setting: ");
  Serial.print(DIPSwitchSetting);
  Serial.println(SettingsText);

  return DIPSwitchSetting;
}
```

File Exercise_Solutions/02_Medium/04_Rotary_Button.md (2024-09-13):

```C++
#define version "1"

//LED for signal indication
#define LEDPin D12

//Rotary Encoder Definitions
#define encAPin D3
#define encBPin D4
#define encButtonPin D2

#define FW 1 //code for forward direction rotation
#define BW -1 //same for backwards

int ButtonState = 0;
volatile int Direction = 0;
volatile byte RotationDetected = false;
volatile int counter = 0;

volatile byte ButtonPushDetected = false;

volatile unsigned long last_time;  // for debouncing

void DetectButtonPush() {
  ButtonPushDetected = true;
}

void DetectRotation() {
  if ((millis() - last_time) < 50)  // debounce time is 50ms
    return;
  RotationDetected = true;
  if (digitalRead(encAPin) == digitalRead(encBPin)) {
    Direction = BW;
    if (counter >= 1) {
      counter--;
    }
  } else {
    Direction = FW;
    if (counter <= 6) {
      counter++;
      }
    }
  last_time = millis();
}

void setup() {
  Serial.begin(115200);
  Serial.print("BITboy Interface Version ");
  Serial.println(version);
  pinMode(encAPin, INPUT_PULLUP);
  pinMode(encBPin, INPUT_PULLUP);
  pinMode(encButtonPin, INPUT_PULLUP);
  pinMode(LEDPin, OUTPUT);
  //Attach an Interrupt to the Rotary Encoder and Button Pins
  attachInterrupt(digitalPinToInterrupt(encButtonPin), DetectButtonPush, CHANGE);
  attachInterrupt(digitalPinToInterrupt(encAPin), DetectRotation, FALLING);
}

void loop() {
  RotationAction();
  ButtonAction();
}

void RotationAction() {
  if (RotationDetected == true) {
    Serial.print("Direction: ");
    Serial.print(Direction);
    Serial.print(" Counter: ");
    Serial.println(counter);
    RotationDetected = !RotationDetected;
  } else if (RotationDetected == false) {
    return;
  }
}

void ButtonAction() {
  ButtonState = digitalRead(encButtonPin);
    if (ButtonState == HIGH) {
      digitalWrite(LEDPin, LOW);
      //Serial.println("button released");
    } else {
      digitalWrite(LEDPin, HIGH);
      //Serial.println("button pushed");
    }
}
```

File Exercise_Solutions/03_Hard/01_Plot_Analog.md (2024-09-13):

```C++
#define version "1"

#include "Arduino_LED_Matrix.h"

#define AnalogDataPin A0
#define DigitalDataPin D5

uint8_t CurrentFrame[8][12];

uint8_t NextFrame[8][12];

uint8_t BootScreen[8][12] = {
  { 0, 0, 0, 0, 0, 0, 1, 0, 0, 0, 0, 0 },
  { 0, 0, 0, 0, 0, 1, 1, 0, 0, 0, 0, 0 },
  { 0, 0, 0, 0, 1, 0, 1, 0, 0, 0, 0, 0 },
  { 0, 0, 0, 0, 1, 0, 1, 0, 0, 0, 0, 0 },
  { 0, 0, 0, 1, 0, 0, 1, 0, 0, 0, 0, 0 },
  { 1, 1, 1, 1, 0, 0, 1, 0, 1, 1, 1, 1 },
  { 0, 0, 0, 0, 0, 0, 1, 1, 0, 0, 0, 0 },
  { 0, 0, 0, 0, 0, 0, 1, 0, 0, 0, 0, 0 }
};

//Initialising variables for later use in the script
int MeasuredAnalogInput;

int PlottingValue;

ArduinoLEDMatrix matrix;

void setup() {
  //Setting the resolution to 12 will read in a range of 0-4095, while setting to 10 will read 0-1023
  analogReadResolution(12);
  pinMode(AnalogDataPin, INPUT);

  //Start serial communication

  matrix.begin();
  matrix.renderBitmap(BootScreen, 8, 12);
  delay(1500);

  Serial.begin(115200);
  Serial.print("BITboy Interface Version ");
  Serial.println(version);
}

void loop() {
    readAnalogSignalInput();
    calcNextFrame();
    matrix.renderBitmap(CurrentFrame, 8, 12);
    delay(100);
}

void readAnalogSignalInput() {
    //Reaging analog input and mapping it to 5V for serial print with accurate units.
  MeasuredAnalogInput = map(analogRead(AnalogDataPin), 0, 4095, 7, 0);
  MeasuredAnalogInput = constrain(MeasuredAnalogInput, 0, 7);

  delay(200);

  //Serial printing of analog signal. The first print will allow to name the variable in the serial plotter.
  Serial.print("Analog_In[V]:");
  Serial.println(MeasuredAnalogInput);

}

void MakeAxis(){
  for (int thisRow = 0; thisRow <= 7; thisRow++) {
    NextFrame[thisRow][0] = 1;
  }
}

void calcNextFrame() {
    PlottingValue = MeasuredAnalogInput;
  for (int thisRow = 0; thisRow <= 7; thisRow++) {
    for (int thisColumn = 0; thisColumn <= 11; thisColumn++) {
      NextFrame[thisRow][thisColumn] = CurrentFrame[thisRow][thisColumn+1];
    }
  }

  for (int thisRow = 0; thisRow <= 7; thisRow++) {
    NextFrame[thisRow][11] = 0;
  }

  NextFrame[PlottingValue][11] = 1;
  MakeAxis();
  
  for (int thisRow = 0; thisRow <= 7; thisRow++) {
    for (int thisColumn = 0; thisColumn <= 11; thisColumn++) {
      CurrentFrame[thisRow][thisColumn] = NextFrame[thisRow][thisColumn];
    }
  }
}
```

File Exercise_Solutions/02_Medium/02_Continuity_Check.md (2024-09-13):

```C++
//Continuity Check Pin
#define ContinuityPin A3

//Buzzer 
#define BuzzerPin D11

//Define Note for Continuity Signal
#define NOTE_D7  2349

int ContinuityStatus = 0;

void setup() {
    pinMode(ContinuityPin, INPUT);
    pinMode(BuzzerPin, OUTPUT);

    tone(BuzzerPin, NOTE_D7, 100);
    delay(100);
    noTone(BuzzerPin);
}

void loop() {
    ContinuityStatus = digitalRead(ContinuityPin);

    if (ContinuityStatus == HIGH) {
    tone(BuzzerPin, NOTE_D7);
    
    } else if (ContinuityStatus == LOW) {
        noTone(BuzzerPin);
    }
}
```

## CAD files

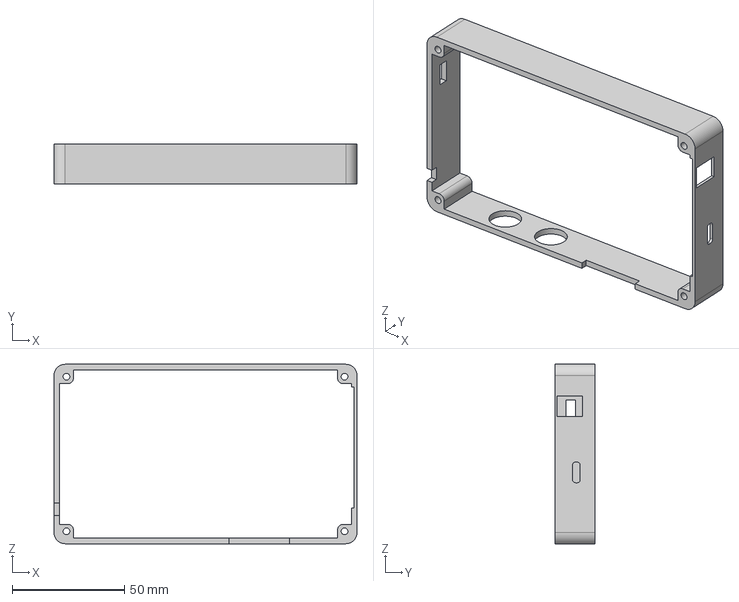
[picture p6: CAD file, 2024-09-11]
Case/BITboy_Case.step
135.0 x 18.0 x 80.0 mm

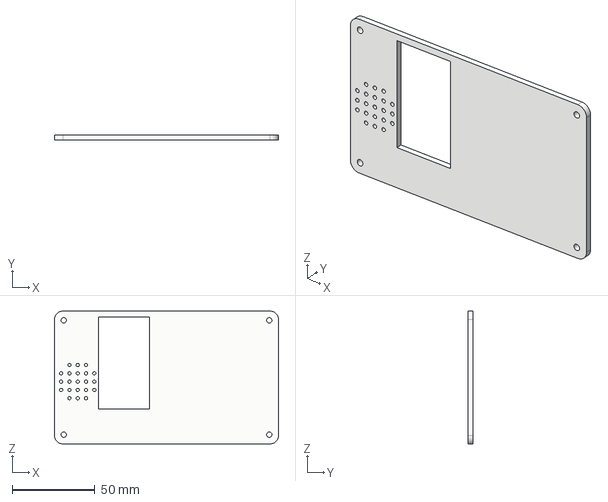
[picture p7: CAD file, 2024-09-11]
Case/BITboy_Acrylic_Cover.step
135.0 x 3.00 x 80.0 mm

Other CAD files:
Case/BITboy_Acrylic_Cover.dxf
Case/BITboy_Acrylic_Cover.stl
Case/BITboy_Case.stl

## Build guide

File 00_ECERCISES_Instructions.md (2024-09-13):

# Exercises

We prepared a collection of exercises as a guide through different communication channels of laboratory instruments: digital signals, analog signals and serial communication. These exercises are increase in difficulty from easy, medium, to hard. First, individual functional modules of the device will be adressed, later they will be combined for interoperability. Working throuhg them in a sequential manner will allow you to build up the know-how required to generate the complete firmware. 

This course will therefore provide essential knowledge for implementing and trouble-shooting experimental setups for neuroscience. As a bonus, the resulting device will be a handy companion for future laboratory projects.

You will have to install the Arudino IDE and copy paste the code from GitHub to the sketch area in the GUI.

[Download Arduino IDE](https://www.arduino.cc/en/software)

In some cases Arduino IDE will require installation of additional drivers for the Arduino UNO rev4 board. This will happen automatically. Connecting the Arduino via USB will allow to select the corresponding serial port, compile and upload the sketch code.

General disclaimer: Our BITboy is designed to work in a range of 0-5V and will take damage if connected to higher loads. Therefore, please be careful. We are planning a future version with overvoltage protection.

Useful Resources
--------------------

Here you can find a complete language reference, built in functions, variable types and structural operators:

[Arduino Language Reference](https://www.arduino.cc/reference/en/)

To complete all exercises, you will have to master functions in Arduino. They can be used to create custom functions but also to pass parameters along and return data:

[Using functions in a sketch](https://docs.arduino.cc/learn/programming/functions/)

Serial Printing is your most powerful debugging tool when coding your device:

[Arduino serial communication](https://www.arduino.cc/reference/en/language/functions/communication/serial/)

In some cases you will have to use the Serial Plotter and/or Serial Monitor of the Arduino IDE:

Tools > Serial Plotter

Tools > Serial Monitor

## Exercises Easy

Here you can make the individual modules work and get some first exposure.

[Go To Exercises Easy](01_EXERCISES_easy.md)

### 1. Make the LED Blink

### 2. Make the Buzzer Beep (or Play a Melody if you feel like it)

### 3. Write Analog or Digital Signals and Test them on the Oscilloscope

### 4. Plot an Image on the LED Matrix (or display an animation if you feel like it)

## Exercises Medium

Here modues with more complex functionality are implemented and in some cases integrated.

[Go To Exercises Medium](02_EXERCISES_medium.md)

### 1. Read an Analog or Digital Signal and Plot it via Serial Communication

### 2. Implement the Continuity Check

### 3. Implement the DIP Switch

### 4. Implement the Rotary Encoder with Button

## Exercises Hard

At this point you will build upon the previous exercises and make all functions work together. It will be essential to implement Arduino functions with returns for global interacting modules. For example, each fuctional module of the device can be handled as an indepenent library.

You can save code in a separate .h file and include it as follows:

```C++
#include "DIPSwitch.h"
```

In the upper right corner of the Arduino IDE click on "..." and select new tab. You can rename it to DIPSwitch.h to generate an external file with additional code.

This will allow you to create configuration functions for each module and include them in void setup of the main sketch file. In addition zou can create functions for void loop that pass on parameters via return.

[Go To Exercises Hard](03_EXERCISES_hard.md)

### 1. Read an Analog or Digital and Plot it on the LED Matrix Display

### 2. Combine All Modules and Make them Work Together

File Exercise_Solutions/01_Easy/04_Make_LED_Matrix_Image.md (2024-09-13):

```C++
#include "Arduino_LED_Matrix.h"

uint8_t BootScreen[8][12] = {
  { 0, 0, 0, 0, 0, 0, 1, 0, 0, 0, 0, 0 },
  { 0, 0, 0, 0, 0, 1, 1, 0, 0, 0, 0, 0 },
  { 0, 0, 0, 0, 1, 0, 1, 0, 0, 0, 0, 0 },
  { 0, 0, 0, 0, 1, 0, 1, 0, 0, 0, 0, 0 },
  { 0, 0, 0, 1, 0, 0, 1, 0, 0, 0, 0, 0 },
  { 1, 1, 1, 1, 0, 0, 1, 0, 1, 1, 1, 1 },
  { 0, 0, 0, 0, 0, 0, 1, 1, 0, 0, 0, 0 },
  { 0, 0, 0, 0, 0, 0, 1, 0, 0, 0, 0, 0 }
};

ArduinoLEDMatrix matrix;

void setup() {
  // put your setup code here, to run once:
  Serial.begin(115200);
  matrix.begin();
}

void loop() {
  // put your main code here, to run repeatedly:
  matrix.renderBitmap(BootScreen, 8, 12);
}
```

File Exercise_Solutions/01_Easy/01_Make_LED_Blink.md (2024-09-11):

```C++
#define ledPin 12 // LED connected to digital pin 13, we define it as a constant value here.

//Instead of defining a constant value, one can also define a variable.

//int ledPin = 12;              

void setup() {
  pinMode(ledPin, OUTPUT);    // sets the digital pin as output
}

void loop() {
  digitalWrite(ledPin, HIGH); // sets the LED on
  delay(1000);                // waits for a second
  digitalWrite(ledPin, LOW);  // sets the LED off
  delay(1000);                // waits for a second
}
```

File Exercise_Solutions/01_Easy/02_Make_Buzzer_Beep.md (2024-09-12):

```C++
//Defining the note D7
#define NOTE_D7  2349

//Buzzer pin is on D11
#define BuzzerPin D11

void setup() {
  // put your setup code here, to run once:
  // use semicolons after each line!
  pinMode(BuzzerPin, OUTPUT);

}

void loop() {
  // put your main code here, to run repeatedly:
  // use semicolons after each line!
  tone(BuzzerPin, NOTE_D7, 100);
  delay(100);
  noTone(BuzzerPin);
  delay(100);
}
```

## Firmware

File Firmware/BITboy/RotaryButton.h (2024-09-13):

//Rotary Encoder Definitions
#define encAPin 3
#define encBPin 4
#define encButtonPin 2

#define FW 1 //code for forward direction rotation
#define BW -1 //same for backwards

volatile int Direction = 0;
volatile byte RotationDetected = false;
volatile int counter = 0;

volatile byte ButtonPushDetected = false;

volatile unsigned long last_time;  // for debouncing


  
int ToggleCounter = 0;
int Toggle = false;
int ConstantAnalogOut = false;
int ConstantDigitalOut = false;
int DigitalOutputValue = 0;
int AnalogOutputValue = 0;

void ButtonAction(int OutputMode) {
  int ButtonState = 0;
  

  if (ButtonPushDetected==true) {
    if (OutputMode == 0) {// Digital Out Const
      ToggleCounter = ToggleCounter + 1;
      if (ToggleCounter == 2) {
        Toggle =! Toggle;
        if (Toggle == true) {
          DigitalOutputValue = 1;
          digitalWrite(LEDPin, HIGH);
          WriteIO(OutputMode, DigitalOutputValue);
          ToggleCounter = 0;
          ConstantDigitalOut = true;
        } else if (Toggle == false) {
          DigitalOutputValue = 0;
          digitalWrite(LEDPin, LOW);
          WriteIO(OutputMode, DigitalOutputValue);
          ConstantDigitalOut = false;
          ToggleCounter = 0;
        } 
      }
    } else if (OutputMode == 1) {// Analog Out Const
    ToggleCounter = ToggleCounter + 1;
      if (ToggleCounter == 2) {
        Toggle =! Toggle;
        if (Toggle == true) {
          AnalogOutputValue = map(counter, 0, 7, 0, 255);
          AnalogOutputValue = constrain(AnalogOutputValue, 0, 255);
          digitalWrite(LEDPin, HIGH);
          WriteIO(OutputMode, AnalogOutputValue);
          ToggleCounter = 0;
          AnalogOutputValue = 1;
          ConstantAnalogOut = true;
        } else if (Toggle == false) {
          AnalogOutputValue = 0;
          AnalogOutputValue = map(AnalogOutputValue, 0, 7, 0, 255);
          AnalogOutputValue = constrain(AnalogOutputValue, 0, 255);
          digitalWrite(LEDPin, LOW);
          WriteIO(OutputMode, AnalogOutputValue);
          ToggleCounter = 0;
          AnalogOutputValue = 0;
          ConstantAnalogOut = false;
        }
      }
    } else if (OutputMode == 4) {// digital pulse
      ButtonState = digitalRead(encButtonPin);
      if (ButtonState == HIGH) {
        DigitalOutputValue = 0;
        digitalWrite(LEDPin, LOW);
        WriteIO(OutputMode, DigitalOutputValue);
      } else {
        DigitalOutputValue = 1;
        digitalWrite(LEDPin, HIGH);
        WriteIO(OutputMode, DigitalOutputValue);
      }
    } else if (OutputMode == 5) {// analog pulse
      ButtonState = digitalRead(encButtonPin);
      if (ButtonState == HIGH) {
        AnalogOutputValue = 0;
        digitalWrite(LEDPin, LOW);
        WriteIO(OutputMode, AnalogOutputValue);
      } else {
        AnalogOutputValue = map(counter, 0, 7, 0, 255);
        AnalogOutputValue = constrain(AnalogOutputValue, 0, 255);
        digitalWrite(LEDPin, HIGH);
        WriteIO(OutputMode, AnalogOutputValue);
      }
    } else if (OutputMode == 2 || OutputMode == 3 || OutputMode == 6 || OutputMode == 7) {
    return;
    }
    ButtonPushDetected = !ButtonPushDetected;
  } else {
    return;
  }
}  


int UpdateConstantAnalogOutput(int ConstAOMode) {
  if (ConstAOMode == 1 && ConstantAnalogOut == true) {
    //int AnalogOutVal = 0;
    AnalogOutputValue = map(counter, 0, 7, 0, 255);
    AnalogOutputValue = constrain(AnalogOutputValue, 0, 255);
    digitalWrite(LEDPin, HIGH);
    WriteIO(ConstAOMode, AnalogOutputValue);
  }
}



int ReadOutput(int ReadOutMode) {
  int MeasuredOutput = 0;
  if (ReadOutMode == 4) {
    //for digital pulse
    MeasuredOutput = DigitalOutputValue;
    MeasuredOutput = map(MeasuredOutput, 0, 1, 0, 5);
    MeasuredOutput = constrain(MeasuredOutput, 0, 5);
  } else if (ReadOutMode == 0) {
    //for digital out constant
    MeasuredOutput = DigitalOutputValue;
    MeasuredOutput = map(MeasuredOutput, 0, 1, 0, 5);
    MeasuredOutput = constrain(MeasuredOutput, 0, 5);
  } else if (ReadOutMode == 1) {
    //for all analog output modes
    MeasuredOutput = AnalogOutputValue;
    MeasuredOutput = map(MeasuredOutput, 0, 255, 0, 5);
    MeasuredOutput = constrain(MeasuredOutput, 0, 5);
  } else if (ReadOutMode == 5) {
    //for all analog output modes
    MeasuredOutput = AnalogOutputValue;
    MeasuredOutput = map(MeasuredOutput, 0, 255, 0, 5);
    MeasuredOutput = constrain(MeasuredOutput, 0, 5);
  }
  return MeasuredOutput;
}

int ReadOutputForDisplay(int ReadOutMode) {
  int MeasuredOutput = 0;
  if (ReadOutMode == 4) {
    //for digital pulse
    MeasuredOutput = DigitalOutputValue;
    MeasuredOutput = map(MeasuredOutput, 0, 1, 7, 0);
    MeasuredOutput = constrain(MeasuredOutput, 0, 7);
  } else if (ReadOutMode == 0) {
    //for digital out constant
    MeasuredOutput = DigitalOutputValue;
    MeasuredOutput = map(MeasuredOutput, 0, 1, 7, 0);
    MeasuredOutput = constrain(MeasuredOutput, 0, 7);
  } else if (ReadOutMode == 1) {
    //for all analog output modes
    MeasuredOutput = counter;
    MeasuredOutput = map(MeasuredOutput, 0, 7, 7, 0);
    MeasuredOutput = constrain(MeasuredOutput, 0, 7);
  } else if (ReadOutMode == 5) {
    //for all analog output modes
    MeasuredOutput = counter;
    MeasuredOutput = map(MeasuredOutput, 0, 7, 7, 0);
    MeasuredOutput = constrain(MeasuredOutput, 0, 7);
  }
  return MeasuredOutput;
}

void DetectButtonPush() {
  ButtonPushDetected = true;
}

void RotationAction() {
  if (RotationDetected == true) {
    RotationDetected = !RotationDetected;
  } else if (RotationDetected == false) {
    return;
  }
}

void DetectRotation() {
  if ((millis() - last_time) < 50)  // debounce time is 50ms
    return;
  RotationDetected = true;
  if (digitalRead(encAPin) == digitalRead(encBPin)) {
    Direction = BW;
    if (counter >= 1) {
      counter--;
    }
  } else {
    Direction = FW;
    if (counter <= 6) {
      counter++;
      }
    }
  last_time = millis();
}

void ConfigRotaryButton() {
  pinMode(encAPin, INPUT_PULLUP);
  pinMode(encBPin, INPUT_PULLUP);
  pinMode(encButtonPin, INPUT_PULLUP);
  attachInterrupt(digitalPinToInterrupt(encButtonPin), DetectButtonPush, CHANGE);
  attachInterrupt(digitalPinToInterrupt(encAPin), DetectRotation, FALLING);
}

int TemporalResolution(int ResolutionMode) {
  int AdaptedDelay = 0;
  if (ResolutionMode == 2 || ResolutionMode == 3 || ResolutionMode == 6 || ResolutionMode == 7) {
    AdaptedDelay = map(counter, 0, 7, 1, 100);
    //AdaptedDelay = constrain(AdaptedDelay, 0, 1000);
  } else if (DIPSwitchSetting == 1) {
    AdaptedDelay = 50;
  } else if (DIPSwitchSetting == 5) {
    AdaptedDelay = 50;
  } else {
    AdaptedDelay = 1;
  }
  return AdaptedDelay;
}

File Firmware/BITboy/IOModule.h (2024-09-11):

//BNC Port Definitions
#define AnalogDataPin A0
#define DigitalDataPin D5

void ConfigIO(int IOMode) {
  if (IOMode == 2 || IOMode == 6  || IOMode == 3  || IOMode == 7) {
    //for all input modes 0 1 4 5
    analogReadResolution(12);
    pinMode(AnalogDataPin, INPUT);
    pinMode(DigitalDataPin, INPUT);
  } else if (IOMode == 0 || IOMode == 1  || IOMode == 4  || IOMode == 5) {
    //for all output modes 2 6 3 7
    pinMode(AnalogDataPin, OUTPUT);
    pinMode(DigitalDataPin, OUTPUT);
  }
}

int ReadIOForDisplay(int InMode) {
  int MeasuredInput;
  if (InMode == 2 || InMode == 6) {
    //for all digital input modes
    MeasuredInput = map(digitalRead(DigitalDataPin), 0, 1, 7, 0);
    MeasuredInput = constrain(MeasuredInput, 0, 7);
  } else if (InMode == 3 || InMode == 7) {
    //for all analog input modes
    MeasuredInput = map(analogRead(AnalogDataPin), 0, 4095, 7, 0); //4095
    MeasuredInput = constrain(MeasuredInput, 0, 7);
  } 
  return MeasuredInput;
}

float ReadIO(int InMode) {
  float MeasuredInput = 0.00;
  if (InMode == 2 || InMode == 6) {
    //for all digital input modes
    MeasuredInput = map(digitalRead(DigitalDataPin), 0, 1, 0, 5);
    MeasuredInput = constrain(MeasuredInput, 0, 5);
  } else if (InMode == 3 || InMode == 7) {
    //for all analog input modes
    MeasuredInput = analogRead(AnalogDataPin);
    MeasuredInput = mapfloat(MeasuredInput, 0, 4095, 0, 5); //4095
  } 
  return MeasuredInput;
}

int WriteIO(int OutMode, int value) {
  if (OutMode == 0 || OutMode == 4) {
    //for all digital output modes
    digitalWrite(DigitalDataPin, value); //HIGH LOW
  } else if (OutMode == 1 || OutMode == 5) {
    //for all analog output modes
    analogWrite(AnalogDataPin, value); //0-255
  }
}
